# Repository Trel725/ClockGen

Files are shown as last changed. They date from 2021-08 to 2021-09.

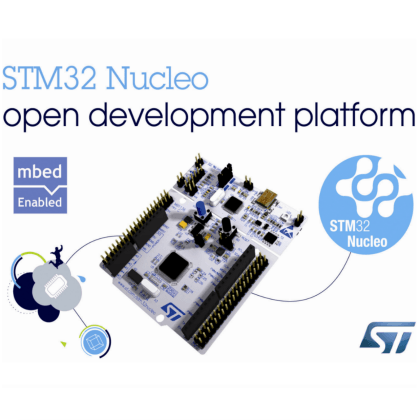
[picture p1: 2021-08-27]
hardware/PCBs/3V3_to_5/meta/board_stm32_nucleo_64.png

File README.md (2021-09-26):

# ClockGen

## What's that?

ClockGen is a project, devoted to developing a device that allow simple synchronization of scientific equipment. When experiments require synchronization, one might select do it with Arduino or similar hardware (LabJack?) which would give millisecond accuracy, or go far beyond that to specialized timing equipment, able of generating nanosecond precise pulses and costing thousands of euro. The goal of that project is to provide "something in between", a device which can provide microsecond accuracy at reasonable price. The devise is based on STM32F446RET Nucleo development board (price below 20 euro).

## Features?

 - Generating square wave at frequencies from 610 Hz (for 16 bit timer) or 0.009 Hz (for 32 bit timer) up to ~ 10 MHz
 - Programming arbitrary sequences of start, stop or change frequency events at 1 us accuracy 
 - Support of up to 10 timer channels for generating square wave
 - Synchronization of the generated signals with nanosecond accuracy by hardware synchronization
 - Up to 22 digital outputs, programmable to generate arbitrary sequences of on/off events with 1 us accuracy and nanosecond synchronization 
 - Hardware extension for Nucleo development board, converting LVTTL signals from microcontroller (3.3V) to standard TTL (5V)
 - Add-on hardware extension, converting 5V TTL signals to high-voltage signals (7-18V).

## How to use it

```python
from clockgen import ProgramGen
from clockgen.interface import TIM, GPIO
from clockgen.utils import send_program, start_execution

#instantiate HW
tim2 = TIM("TIM2")
tim5 = TIM("TIM5")
gpa = GPIO("GPIOA")

# turn on both timers at time 100us from program start
# tim2 at 20 kHz
tim2.on_sync(20_000, 100)
# and tim5 at 10 kHz
tim5.on_sync(10_000, 100)
# start them synchnously
tim2.start_sync(100)

# set 4th and 5th pins in GPIOA to high level at 120 us
gpa.on([4, 5], 120)
# then pin 4 to low level at 150 us
gpa.off(4, 150)
# and pin 5 at 900 us
gpa.off(5, 900)

# finally turn off the timers at 1000 us
tim2.off_sync(1000)
tim5.off_sync(1000)

# instantiate program generator
pg = ProgramGen()
# and generate the program, providing it list of used HW
prog = pg.generate_program([gpa, tim2, tim5])
# open the serial connection
ser = serial.Serial("/dev/ttyACM0", baudrate=1000000, timeout=5)
# and send the program to microntroller
send_program(prog)
# and start its execution:
start_execution()
```

Also, see folder examples.

## How does it work?

1. User describes the desired sequence of operations, like start signal generation at PA0 at 300 us.
2. Host-side program keeps track of all register changes and thus translates high-level operations into low-level
register manipulation
3. Host compiles sequence of register manipilation actions into binary program for micontroller and sends the program.
4. Microcontroller stores the program in RAM and waits for the start_execution command. As soon as command is received, it starts execution and generates required sequence of signals.

## What do I need to start using the ClockGen
In the simpliest case - just STM32F446RET Nucleo development board. As soon as your equipment recognizes LVTTL (3.3V) logical levels, it should suffice. Still, majority of scientific equipment works with 5V TTL levels, and behaviour might be unpredictable if different logical levels is used, thus it is recommeded to get extension board, which converts the signals to 5V TTL. Moreover, it is capable to supply more current and electrically isolates microcontroller from high voltage spikes.

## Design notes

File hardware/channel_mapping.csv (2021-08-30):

l | pin | tim | chan | port
0 | d2 | 1 | 3 | pa10
1 | d6 | 2 | 3 | pb10
2 | d4 | 3 | 2 | pb5
3 | d10 | 4 | 1 | pb6
4 | a0 | 5 | 1 | pa0
5 | d9 | 8 | 2 | pc7 | external clock
6 | d15 | 10 | 1 | pb8 | no slave
7 | d14 | 11 | 1 | pb9 | no slave
8 | d12 | 13 | 1 | pa6 | no slave
9 | d11 | 14 | 1 | pa7 | No slave

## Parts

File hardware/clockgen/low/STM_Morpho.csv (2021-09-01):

Reference | Value | Footprint | Datasheet
CN10 | Conn_02x19_Odd_Even | Connector_PinSocket_2.54mm:PinSocket_2x19_P2.54mm_Vertical | ~
U1 | 74ALVC164245DLG4 | footprints:74ALVC164245DLG4
R1 | 10K | Resistor_THT:R_Axial_DIN0207_L6.3mm_D2.5mm_P2.54mm_Vertical | ~
R2 | 10K | Resistor_THT:R_Axial_DIN0207_L6.3mm_D2.5mm_P2.54mm_Vertical | ~
U2 | 74ALVC164245DLG4 | footprints:74ALVC164245DLG4
C2 | CP | Capacitor_THT:CP_Radial_D5.0mm_P2.00mm | ~
C3.31 | C | Capacitor_SMD:C_0805_2012Metric | ~
C5V1 | C | Capacitor_SMD:C_0805_2012Metric | ~
C5V2 | C | Capacitor_SMD:C_0805_2012Metric | ~
C3.32 | C | Capacitor_SMD:C_0805_2012Metric | ~
C1 | CP | Capacitor_THT:CP_Radial_D5.0mm_P2.00mm | ~
J1 | Conn_02x20_Odd_Even | Connector_PinHeader_2.54mm:PinHeader_2x20_P2.54mm_Vertical | ~
CN7 | Conn_02x19_Odd_Even | Connector_PinSocket_2.54mm:PinSocket_2x19_P2.54mm_Vertical | ~

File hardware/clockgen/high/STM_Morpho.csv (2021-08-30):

Reference | Value | Footprint | Datasheet
U1 | CD40109BNSR | CD40109BNSR:CD40109BNSR
U2 | CD40109BNSR | CD40109BNSR:CD40109BNSR
U3 | CD40109BNSR | CD40109BNSR:CD40109BNSR
U4 | CD40109BNSR | CD40109BNSR:CD40109BNSR
U5 | CD40109BNSR | CD40109BNSR:CD40109BNSR
U6 | CD40109BNSR | CD40109BNSR:CD40109BNSR
U7 | CD40109BNSR | CD40109BNSR:CD40109BNSR
U8 | CD40109BNSR | CD40109BNSR:CD40109BNSR
C4 | CP | Capacitor_THT:CP_Radial_D5.0mm_P2.00mm | ~
CHIGH3 | C | Capacitor_SMD:C_1206_3216Metric | ~
CHIGH6 | C | Capacitor_SMD:C_1206_3216Metric | ~
CHIGH1 | C | Capacitor_SMD:C_1206_3216Metric | ~
CHIGH4 | C | Capacitor_SMD:C_1206_3216Metric | ~
CHIGH7 | C | Capacitor_SMD:C_1206_3216Metric | ~
CHIGH8 | C | Capacitor_SMD:C_1206_3216Metric | ~
CHIGH2 | C | Capacitor_SMD:C_1206_3216Metric | ~
CHIGH5 | C | Capacitor_SMD:C_1206_3216Metric | ~
J2 | Conn_02x20_Odd_Even | Connector_PinHeader_2.54mm:PinHeader_2x20_P2.54mm_Vertical | ~
J1 | Conn_02x20_Odd_Even | Connector_PinHeader_2.54mm:PinHeader_2x20_P2.54mm_Vertical | ~
R1 | 1K | Resistor_THT:R_Axial_DIN0207_L6.3mm_D2.5mm_P2.54mm_Vertical | ~
J3 | Conn_01x02_Female | TerminalBlock_Phoenix:TerminalBlock_Phoenix_PT-1,5-2-3.5-H_1x02_P3.50mm_Horizontal | ~
C1 | CP | Capacitor_THT:CP_Radial_D5.0mm_P2.00mm | ~

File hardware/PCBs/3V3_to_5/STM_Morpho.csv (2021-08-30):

Reference | Value | Footprint | Datasheet
CN10 | Conn_02x19_Odd_Even | Connector_PinSocket_2.54mm:PinSocket_2x19_P2.54mm_Vertical | ~
U1 | 74ALVC164245DLG4 | footprints:74ALVC164245DLG4
R1 | 10K | Resistor_THT:R_Axial_DIN0207_L6.3mm_D2.5mm_P2.54mm_Vertical | ~
R2 | 10K | Resistor_THT:R_Axial_DIN0207_L6.3mm_D2.5mm_P2.54mm_Vertical | ~
U2 | 74ALVC164245DLG4 | footprints:74ALVC164245DLG4
C2 | CP | Capacitor_THT:CP_Radial_D5.0mm_P2.00mm | ~
C3.31 | C | Capacitor_SMD:C_0805_2012Metric | ~
C5V1 | C | Capacitor_SMD:C_0805_2012Metric | ~
C5V2 | C | Capacitor_SMD:C_0805_2012Metric | ~
C3.32 | C | Capacitor_SMD:C_0805_2012Metric | ~
C1 | CP | Capacitor_THT:CP_Radial_D5.0mm_P2.00mm | ~
J1 | Conn_02x20_Odd_Even | Connector_PinHeader_2.54mm:PinHeader_2x20_P2.54mm_Vertical | ~
CN7 | Conn_02x19_Odd_Even | Connector_PinSocket_2.54mm:PinSocket_2x19_P2.54mm_Vertical | ~
J1 | Conn_02x20_Odd_Even | Connector_PinHeader_2.54mm:PinHeader_2x20_P2.54mm_Vertical | ~
J3 | Screw_Terminal_01x08 | TerminalBlock_Phoenix:TerminalBlock_Phoenix_PT-1,5-8-3.5-H_1x08_P3.50mm_Horizontal | ~
J2 | Screw_Terminal_01x08 | TerminalBlock_Phoenix:TerminalBlock_Phoenix_PT-1,5-8-3.5-H_1x08_P3.50mm_Horizontal | ~
J5 | Screw_Terminal_01x08 | TerminalBlock_Phoenix:TerminalBlock_Phoenix_PT-1,5-8-3.5-H_1x08_P3.50mm_Horizontal | ~
J4 | Screw_Terminal_01x08 | TerminalBlock_Phoenix:TerminalBlock_Phoenix_PT-1,5-8-3.5-H_1x08_P3.50mm_Horizontal | ~
J6 | Screw_Terminal_01x08 | TerminalBlock_Phoenix:TerminalBlock_Phoenix_PT-1,5-8-3.5-H_1x08_P3.50mm_Horizontal | ~
J7 | Screw_Terminal_01x08 | TerminalBlock_Phoenix:TerminalBlock_Phoenix_PT-1,5-8-3.5-H_1x08_P3.50mm_Horizontal | ~
J8 | Screw_Terminal_01x08 | TerminalBlock_Phoenix:TerminalBlock_Phoenix_PT-1,5-8-3.5-H_1x08_P3.50mm_Horizontal | ~
J9 | Screw_Terminal_01x08 | TerminalBlock_Phoenix:TerminalBlock_Phoenix_PT-1,5-8-3.5-H_1x08_P3.50mm_Horizontal | ~
U1 | CD40109BNSR | CD40109BNSR:CD40109BNSR
U2 | CD40109BNSR | CD40109BNSR:CD40109BNSR
U3 | CD40109BNSR | CD40109BNSR:CD40109BNSR
U4 | CD40109BNSR | CD40109BNSR:CD40109BNSR
U5 | CD40109BNSR | CD40109BNSR:CD40109BNSR
U6 | CD40109BNSR | CD40109BNSR:CD40109BNSR
U7 | CD40109BNSR | CD40109BNSR:CD40109BNSR
U8 | CD40109BNSR | CD40109BNSR:CD40109BNSR
C4 | CP | Capacitor_THT:CP_Radial_D5.0mm_P2.00mm | ~
CHIGH3 | C | Capacitor_SMD:C_1206_3216Metric | ~
CHIGH6 | C | Capacitor_SMD:C_1206_3216Metric | ~
CHIGH1 | C | Capacitor_SMD:C_1206_3216Metric | ~
CHIGH4 | C | Capacitor_SMD:C_1206_3216Metric | ~
CHIGH7 | C | Capacitor_SMD:C_1206_3216Metric | ~
CHIGH8 | C | Capacitor_SMD:C_1206_3216Metric | ~
CHIGH2 | C | Capacitor_SMD:C_1206_3216Metric | ~
CHIGH5 | C | Capacitor_SMD:C_1206_3216Metric | ~
J2 | Conn_02x20_Odd_Even | Connector_PinHeader_2.54mm:PinHeader_2x20_P2.54mm_Vertical | ~
J1 | Conn_02x20_Odd_Even | Connector_PinHeader_2.54mm:PinHeader_2x20_P2.54mm_Vertical | ~
R1 | 1K | Resistor_THT:R_Axial_DIN0207_L6.3mm_D2.5mm_P2.54mm_Vertical | ~
J3 | Conn_01x02_Female | TerminalBlock_Phoenix:TerminalBlock_Phoenix_PT-1,5-2-3.5-H_1x02_P3.50mm_Horizontal | ~
C1 | CP | Capacitor_THT:CP_Radial_D5.0mm_P2.00mm | ~

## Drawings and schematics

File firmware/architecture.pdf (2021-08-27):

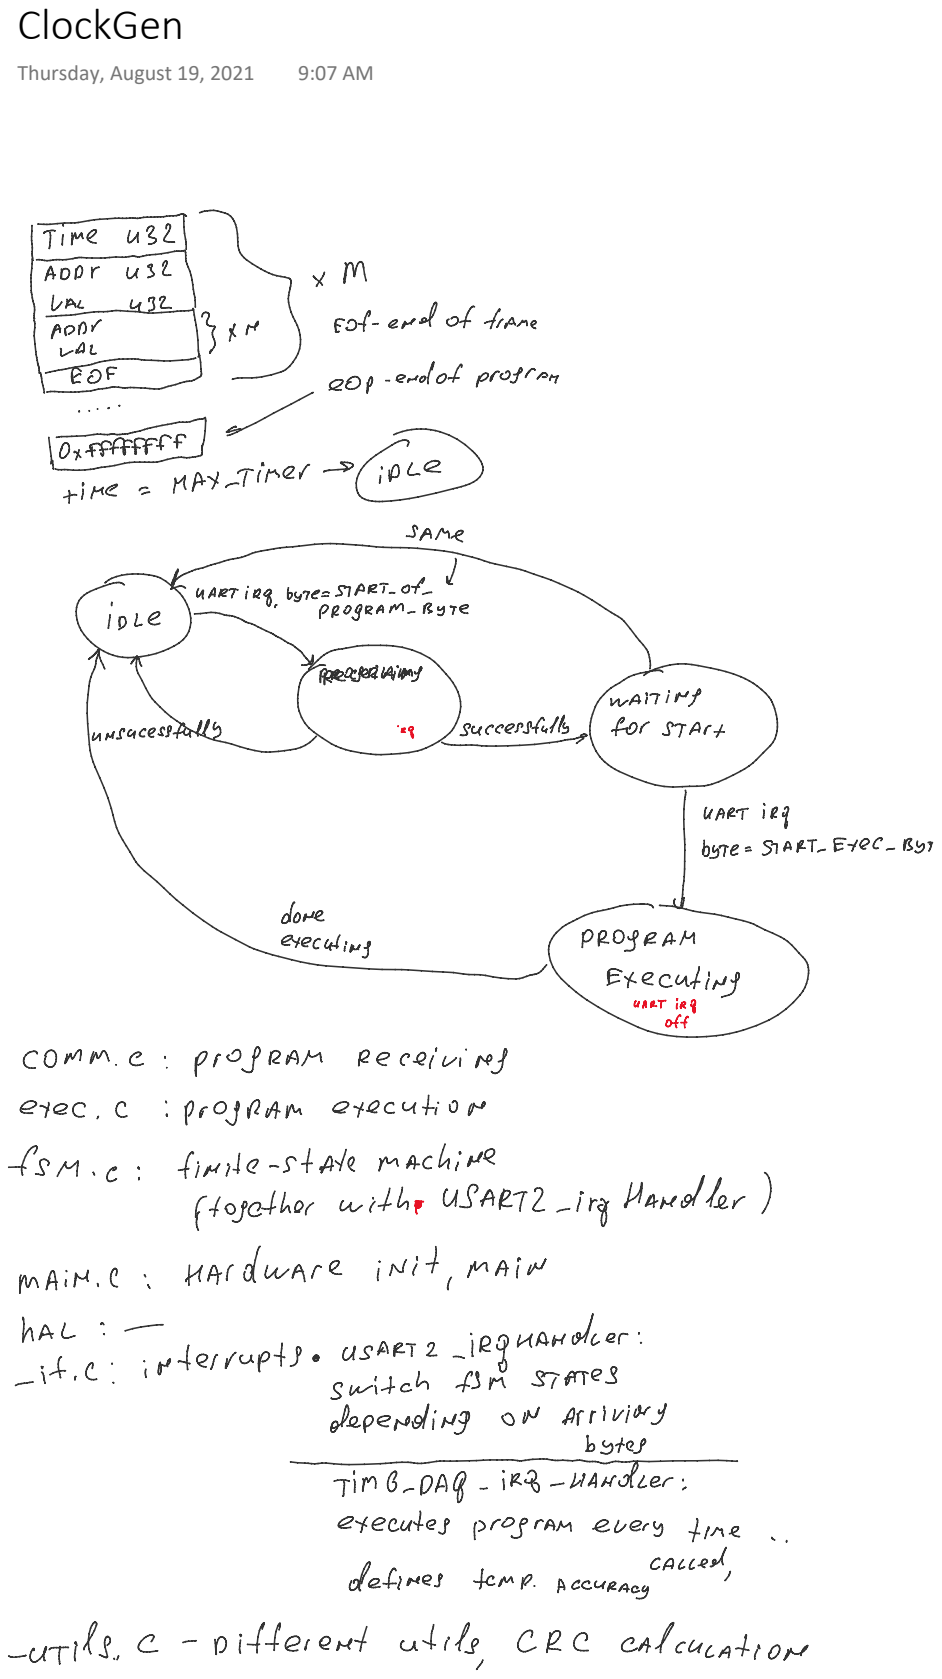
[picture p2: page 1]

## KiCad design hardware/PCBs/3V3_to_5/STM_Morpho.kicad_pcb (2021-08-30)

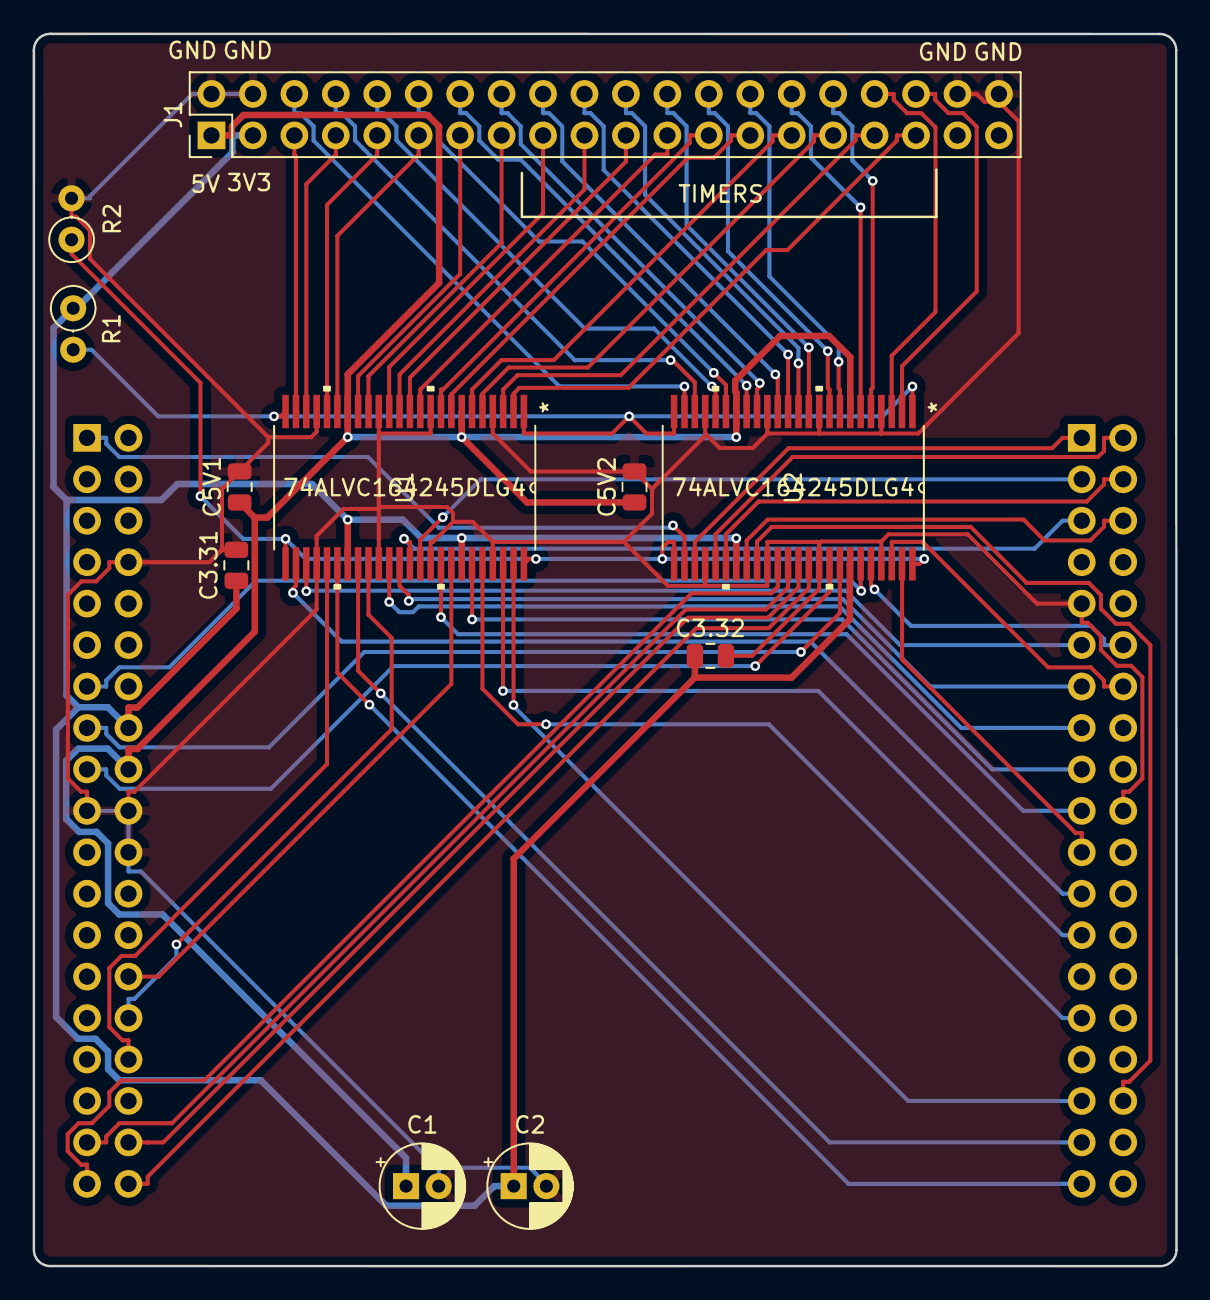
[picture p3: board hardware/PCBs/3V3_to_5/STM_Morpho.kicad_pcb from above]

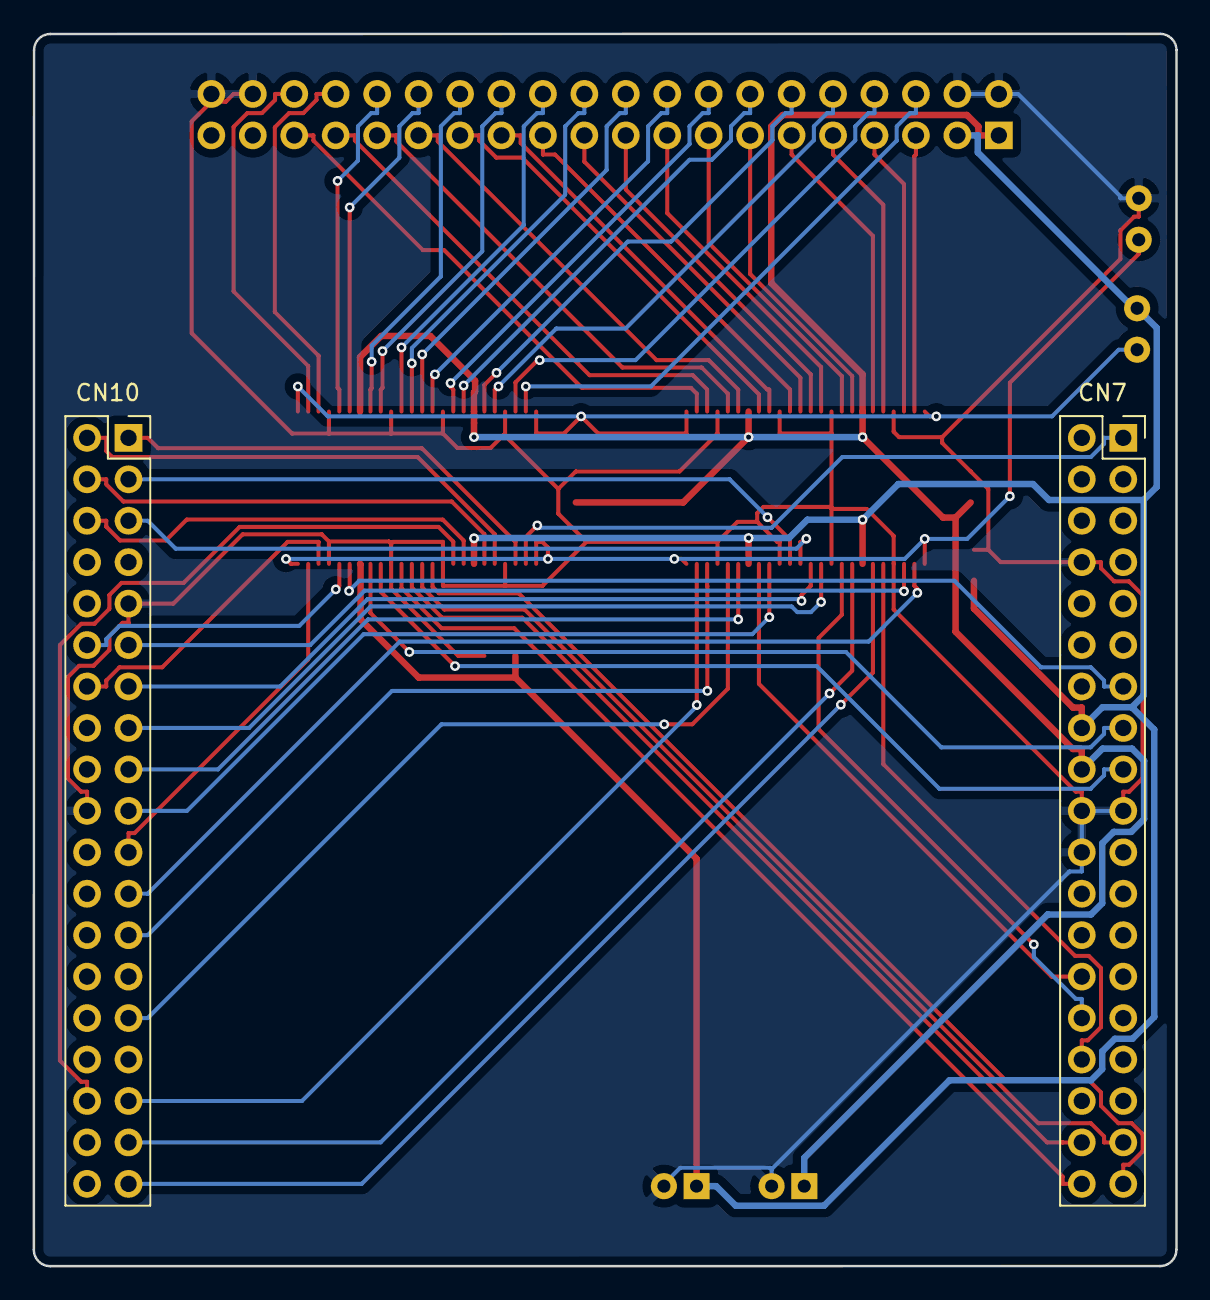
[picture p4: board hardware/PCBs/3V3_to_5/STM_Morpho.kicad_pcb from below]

Board: 2 copper layers, 70.0 x 75.5 mm, 13 parts (2 on the bottom side), 69 nets.

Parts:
C1, C2: CP; CP_Radial_D5.0mm_P2.00mm
C3.31, C3.32, C5V1, C5V2: C; C_0805_2012Metric
CN7, CN10: Conn_02x19_Odd_Even; PinSocket_2x19_P2.54mm_Vertical
J1: Conn_02x20_Odd_Even; PinHeader_2x20_P2.54mm_Vertical
R1, R2: 10K; R_Axial_DIN0207_L6.3mm_D2.5mm_P2.54mm_Vertical
U1, U2: 74ALVC164245DLG4

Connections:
+3V3: C2.1, C3.31.1, C3.32.1, CN7.16, J1.3, R1.1, U1.31, U1.42, U2.31, U2.42
+5V: C1.1, C5V1.1, C5V2.1, CN7.18, J1.1, U1.7, U1.18, U2.7, U2.18
/PA0: CN7.28, U1.41
/PA0_5V: J1.27, U1.8
/PA1: CN7.30, U1.33
/PA1_5V: J1.15, U1.16
/PA2: CN10.35, U1.32
/PA2_5V: J1.13, U1.17
/PA3: CN10.37, U1.30
/PA3_5V: J1.11, U1.19
/PA4: CN7.32, U1.29
/PA4_5V: J1.9, U1.20
/PA5: CN10.11, U1.27
/PA5_5V: J1.7, U1.22
/PA6: CN10.13, U1.36
/PA6_5V: J1.19, U1.13
/PA7: CN10.15, U1.35
/PA7_5V: J1.17, U1.14
/PA8: CN10.23, U1.26
/PA8_5V: J1.5, U1.23
/PA9: CN10.21, U2.47
/PA9_5V: J1.36, U2.2
/PA10: CN10.33, U1.47
/PA10_5V: J1.35, U1.2
/PA11: CN10.14, U2.46
/PA11_5V: J1.34, U2.3
/PA12: CN10.12, U2.44
/PA12_5V: J1.32, U2.5
/PA13: CN7.13, U2.43
/PA13_5V: J1.30, U2.6
/PA14: CN7.15, U2.41
/PA14_5V: J1.28, U2.8
/PA15: CN7.17, U2.40
/PA15_5V: J1.26, U2.9
/PB5: CN10.29, U1.44
/PB5_5V: J1.31, U1.5
/PB6: CN10.17, U1.43
/PB6_5V: J1.29, U1.6
/PB8: CN10.3, U1.38
/PB8_5V: J1.23, U1.11
/PB9: CN10.5, U1.37
/PB9_5V: J1.21, U1.12
/PB10: CN10.25, U1.46
/PB10_5V: J1.33, U1.3
/PC0: CN7.38, U2.38
/PC0_5V: J1.24, U2.11
/PC1: CN7.36, U2.37
/PC1_5V: J1.22, U2.12
/PC2: CN7.35, U2.36
/PC2_5V: J1.20, U2.13
/PC3: CN7.37, U2.35
/PC3_5V: J1.18, U2.14
/PC4: CN10.34, U2.33
/PC4_5V: J1.16, U2.16
/PC5: CN10.6, U2.32
/PC5_5V: J1.14, U2.17
/PC6: CN10.4, U2.30
/PC6_5V: J1.12, U2.19
/PC7: CN10.19, U1.40
/PC7_5V: J1.25, U1.9
/PC8: CN10.2, U2.29
/PC8_5V: J1.10, U2.20
/PC9: CN10.1, U2.27
/PC9_5V: J1.8, U2.22
/PC10: CN7.1, U2.26
/PC10_5V: J1.6, U2.23
/PULLDOWN: R2.1, U1.25, U1.48, U2.25, U2.48
/PULLUP: R1.2, U1.1, U1.24, U2.1, U2.24
GND: C1.2, C2.2, C3.31.2, C3.32.2, C5V1.2, C5V2.2, CN7.8, CN7.19, CN7.20, CN7.22, CN10.9, CN10.20, J1.2, J1.4, J1.38, J1.40, R2.2, U1.4, U1.10, U1.15, U1.21, U1.28, U1.34, U1.39, U1.45, U2.4, U2.10, U2.15, U2.21, U2.28, U2.34, U2.39, U2.45

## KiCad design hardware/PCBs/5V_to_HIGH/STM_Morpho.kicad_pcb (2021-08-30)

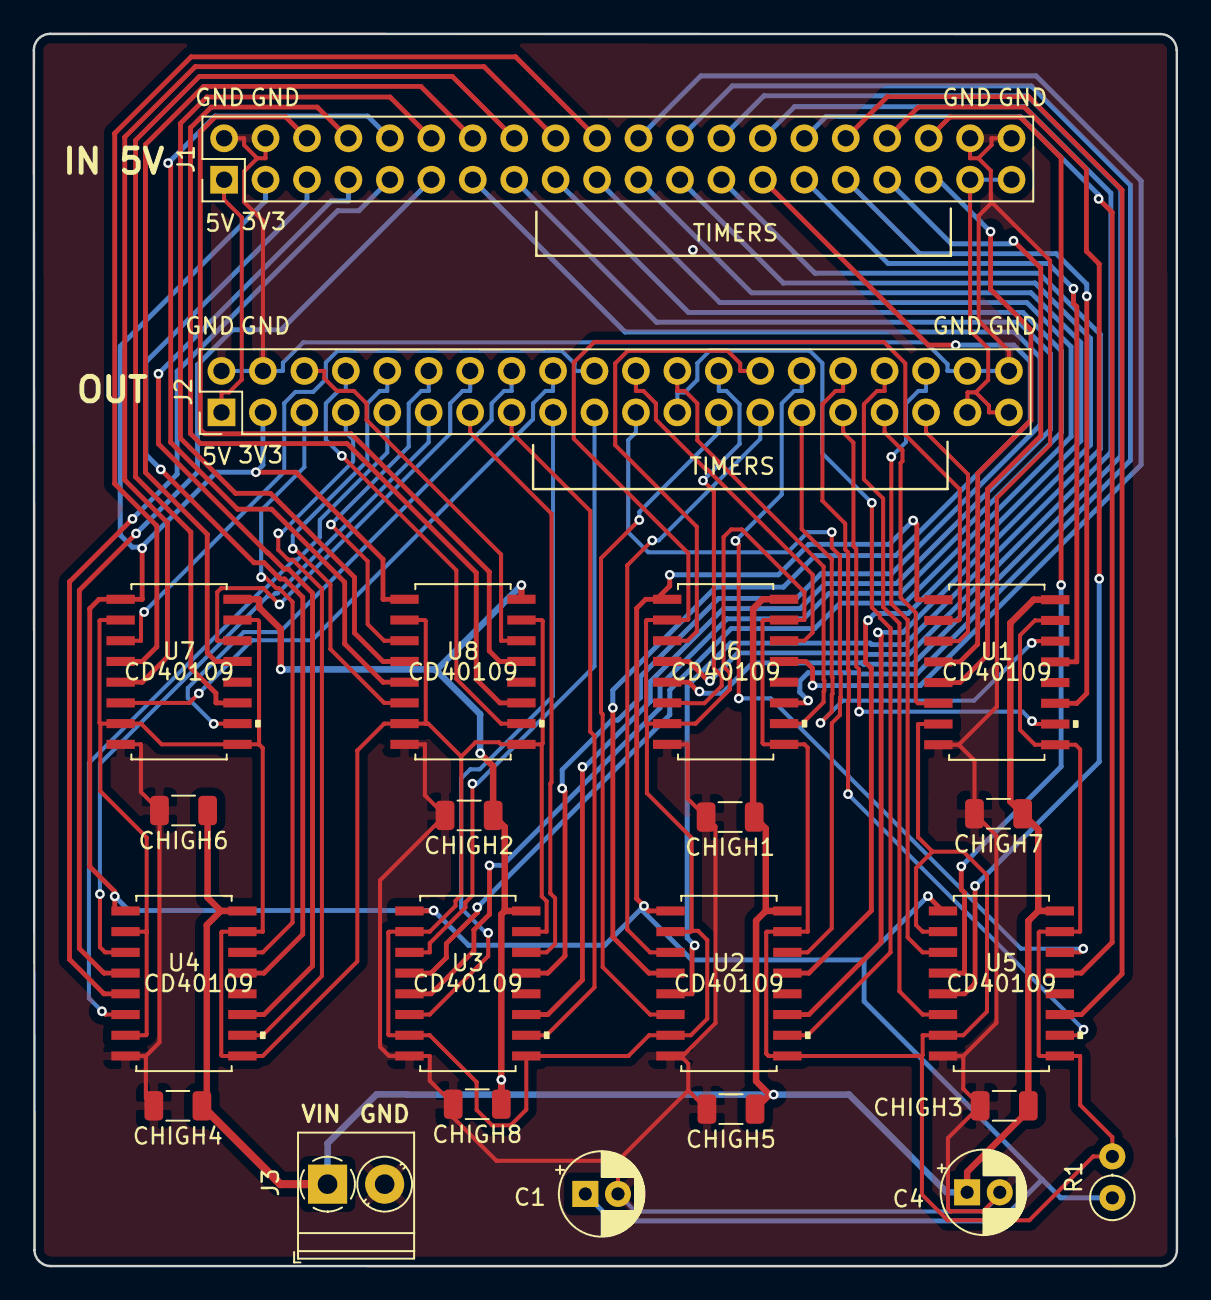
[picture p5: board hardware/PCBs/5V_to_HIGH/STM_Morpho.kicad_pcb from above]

Board: 2 copper layers, 70.1 x 75.5 mm, 22 parts (0 on the bottom side), 70 nets.

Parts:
C1, C4: CP; CP_Radial_D5.0mm_P2.00mm
CHIGH1, CHIGH2, CHIGH3, CHIGH4, CHIGH5, CHIGH6, CHIGH7, CHIGH8: C; C_1206_3216Metric
J1, J2: Conn_02x20_Odd_Even; PinHeader_2x20_P2.54mm_Vertical
J3: Conn_01x02_Female; TerminalBlock_Phoenix_PT-1,5-2-3.5-H_1x02_P3.50mm_Horizontal
R1: 1K; R_Axial_DIN0207_L6.3mm_D2.5mm_P2.54mm_Vertical
U1, U2, U3, U4, U5, U6, U7, U8: CD40109; CD40109BNSR

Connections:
+3V3: C1.1, J1.3, J2.3, R1.1, U1.1, U2.1, U3.1, U4.1, U5.1, U6.1, U7.1, U8.1
+15V: C4.1, CHIGH1.1, CHIGH2.1, CHIGH3.1, CHIGH4.1, CHIGH5.1, CHIGH6.1, CHIGH7.1, CHIGH8.1, J3.1, U1.16, U2.16, U3.16, U4.16, U5.16, U6.16, U7.16, U8.16
/+5V: J1.1, J2.1
/NC: J1.37, J1.39, J2.37, J2.39
/PA0_5V: J2.27, U2.3
/PA0_HIGH: J1.27, U2.4
/PA1_5V: J2.15, U3.10
/PA1_HIGH: J1.15, U3.11
/PA2_5V: J2.13, U3.14
/PA2_HIGH: J1.13, U3.13
/PA3_5V: J2.11, U4.3
/PA3_HIGH: J1.11, U4.4
/PA4_5V: J2.9, U4.6
/PA4_HIGH: J1.9, U4.5
/PA5_5V: J2.7, U4.10
/PA5_HIGH: J1.7, U4.11
/PA6_5V: J2.19, U3.3
/PA6_HIGH: J1.19, U3.4
/PA7_5V: J2.17, U3.6
/PA7_HIGH: J1.17, U3.5
/PA8_5V: J2.5, U4.14
/PA8_HIGH: J1.5, U4.13
/PA9_5V: J2.36, U5.3
/PA9_HIGH: J1.36, U5.4
/PA10_5V: J2.35, U1.3
/PA10_HIGH: J1.35, U1.4
/PA11_5V: J2.34, U5.6
/PA11_HIGH: J1.34, U5.5
/PA12_5V: J2.32, U5.10
/PA12_HIGH: J1.32, U5.11
/PA13_5V: J2.30, U5.14
/PA13_HIGH: J1.30, U5.13
/PA14_5V: J2.28, U6.3
/PA14_HIGH: J1.28, U6.4
/PA15_5V: J2.26, U6.6
/PA15_HIGH: J1.26, U6.5
/PB5_5V: J2.31, U1.10
/PB5_HIGH: J1.31, U1.11
/PB6_5V: J2.29, U1.14
/PB6_HIGH: J1.29, U1.13
/PB8_5V: J2.23, U2.10
/PB8_HIGH: J1.23, U2.11
/PB9_5V: J2.21, U2.14
/PB9_HIGH: J1.21, U2.13
/PB10_5V: J2.33, U1.6
/PB10_HIGH: J1.33, U1.5
/PC0_5V: J2.24, U6.10
/PC0_HIGH: J1.24, U6.11
/PC1_5V: J2.22, U6.14
/PC1_HIGH: J1.22, U6.13
/PC2_5V: J2.20, U7.3
/PC2_HIGH: J1.20, U7.4
/PC3_5V: J2.18, U7.6
/PC3_HIGH: J1.18, U7.5
/PC4_5V: J2.16, U7.10
/PC4_HIGH: J1.16, U7.11
/PC5_5V: J2.14, U7.14
/PC5_HIGH: J1.14, U7.13
/PC6_5V: J2.12, U8.3
/PC6_HIGH: J1.12, U8.4
/PC7_5V: J2.25, U2.6
/PC7_HIGH: J1.25, U2.5
/PC8_5V: J2.10, U8.6
/PC8_HIGH: J1.10, U8.5
/PC9_5V: J2.8, U8.10
/PC9_HIGH: J1.8, U8.11
/PC10_5V: J2.6, U8.14
/PC10_HIGH: J1.6, U8.13
/PULLUP_HIGH: R1.2, U1.2, U1.7, U1.9, U1.15, U2.2, U2.7, U2.9, U2.15, U3.2, U3.7, U3.9, U3.15, U4.2, U4.7, U4.9, U4.15, U5.2, U5.7, U5.9, U5.15, U6.2, U6.7, U6.9, U6.15, U7.2, U7.7, U7.9, U7.15, U8.2, U8.7, U8.9, U8.15
GND: C1.2, C4.2, CHIGH1.2, CHIGH2.2, CHIGH3.2, CHIGH4.2, CHIGH5.2, CHIGH6.2, CHIGH7.2, CHIGH8.2, J1.2, J1.4, J1.38, J1.40, J2.2, J2.4, J2.38, J2.40, J3.2, U1.8, U2.8, U3.8, U4.8, U5.8, U6.8, U7.8, U8.8

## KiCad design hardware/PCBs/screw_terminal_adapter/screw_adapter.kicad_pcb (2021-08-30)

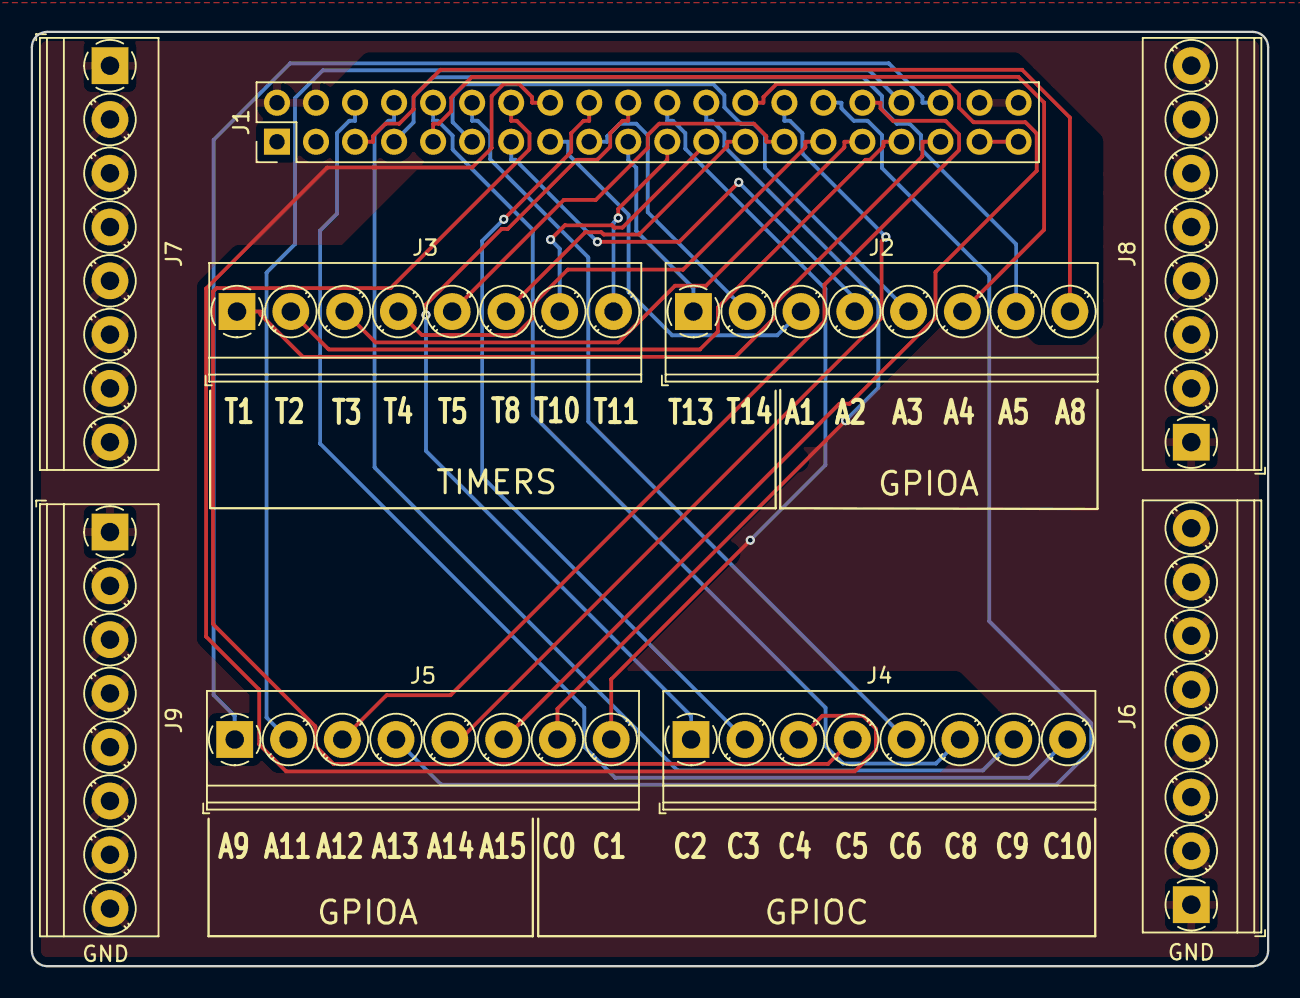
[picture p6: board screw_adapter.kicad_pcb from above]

Board: 2 copper layers, 80.5 x 60.8 mm, 9 parts (0 on the bottom side), 34 nets.

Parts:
J1: Conn_02x20_Odd_Even; PinHeader_2x20_P2.54mm_Vertical
J2, J3, J4, J5, J6, J7, J8, J9: Screw_Terminal_01x08; TerminalBlock_Phoenix_PT-1,5-8-3.5-H_1x08_P3.50mm_Horizontal

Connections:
/NC: J1.37, J1.39
/PA0_5V: J1.27, J3.5
/PA1_5V: J1.15, J2.3
/PA2_5V: J1.13, J2.4
/PA3_5V: J1.11, J2.5
/PA4_5V: J1.9, J2.6
/PA5_5V: J1.7, J2.7
/PA6_5V: J1.19, J2.1
/PA7_5V: J1.17, J2.2
/PA8_5V: J1.5, J2.8
/PA9_5V: J1.36, J5.1
/PA10_5V: J1.35, J3.1
/PA11_5V: J1.34, J5.2
/PA12_5V: J1.32, J5.3
/PA13_5V: J1.30, J5.4
/PA14_5V: J1.28, J5.5
/PA15_5V: J1.26, J5.6
/PB5_5V: J1.31, J3.3
/PB6_5V: J1.29, J3.4
/PB8_5V: J1.23, J3.7
/PB9_5V: J1.21, J3.8
/PB10_5V: J1.33, J3.2
/PC0_5V: J1.24, J5.7
/PC1_5V: J1.22, J5.8
/PC2_5V: J1.20, J4.1
/PC3_5V: J1.18, J4.2
/PC4_5V: J1.16, J4.3
/PC5_5V: J1.14, J4.4
/PC6_5V: J1.12, J4.5
/PC7_5V: J1.25, J3.6
/PC8_5V: J1.10, J4.6
/PC9_5V: J1.8, J4.7
/PC10_5V: J1.6, J4.8
GND: J1.2, J1.4, J1.38, J1.40, J6.1, J6.2, J6.3, J6.4, J6.5, J6.6, J6.7, J6.8, J7.1, J7.2, J7.3, J7.4, J7.5, J7.6, J7.7, J7.8, J8.1, J8.2, J8.3, J8.4, J8.5, J8.6, J8.7, J8.8, J9.1, J9.2, J9.3, J9.4, J9.5, J9.6, J9.7, J9.8

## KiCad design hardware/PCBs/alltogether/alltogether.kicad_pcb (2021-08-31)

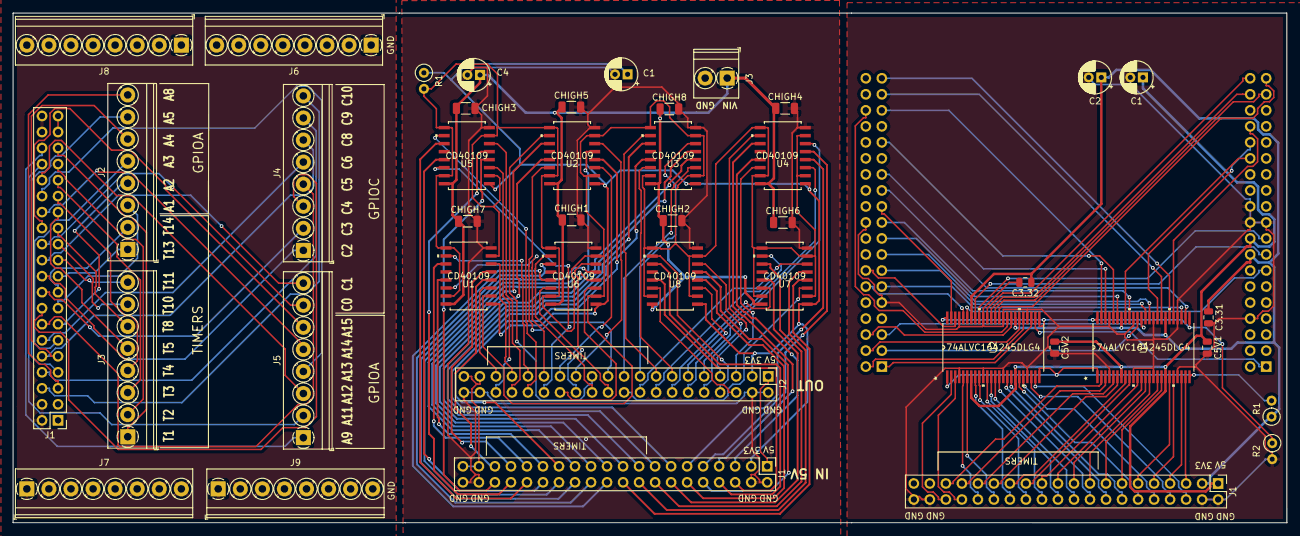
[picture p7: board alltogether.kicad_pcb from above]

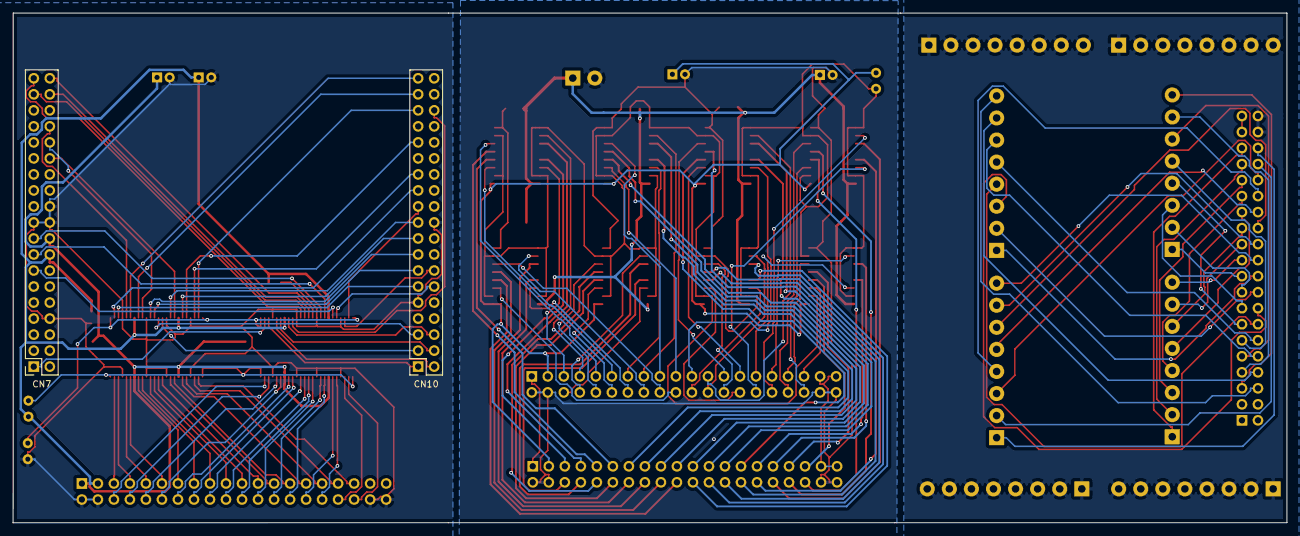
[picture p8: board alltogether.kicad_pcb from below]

Board: 2 copper layers, 202.0 x 80.8 mm, 44 parts (2 on the bottom side), 105 nets.

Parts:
C1, C1#2, C2, C4: CP; CP_Radial_D5.0mm_P2.00mm
C3.31, C3.32, C5V1, C5V2: C; C_0805_2012Metric
CHIGH1, CHIGH2, CHIGH3, CHIGH4, CHIGH5, CHIGH6, CHIGH7, CHIGH8: C; C_1206_3216Metric
CN7, CN10: Conn_02x19_Odd_Even; PinSocket_2x19_P2.54mm_Vertical
J1, J1#2, J1#3, J2#2: Conn_02x20_Odd_Even; PinHeader_2x20_P2.54mm_Vertical
J2, J3, J4, J5, J6, J7, J8, J9: Screw_Terminal_01x08; TerminalBlock_Phoenix_PT-1,5-8-3.5-H_1x08_P3.50mm_Horizontal
J3#2: Conn_01x02_Female; TerminalBlock_Phoenix_PT-1,5-2-3.5-H_1x02_P3.50mm_Horizontal
R1: 1K; R_Axial_DIN0207_L6.3mm_D2.5mm_P2.54mm_Vertical
R1#2, R2: 10K; R_Axial_DIN0207_L6.3mm_D2.5mm_P2.54mm_Vertical
U1, U2, U3, U4, U5, U6, U7, U8: CD40109; CD40109BNSR
U1#2, U2#2: 74ALVC164245DLG4

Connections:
+3V3: C1.1, C2.1, C3.31.1, C3.32.1, CN7.16, J1#2.3, J1#3.3, J2#2.3, R1.1, R1#2.1, U1.1, U1#2.31, U1#2.42, U2.1, U2#2.31, U2#2.42, U3.1, U4.1, U5.1, U6.1, U7.1, U8.1
+5V: C1#2.1, C5V1.1, C5V2.1, CN7.18, J1#3.1, U1#2.7, U1#2.18, U2#2.7, U2#2.18
+15V: C4.1, CHIGH1.1, CHIGH2.1, CHIGH3.1, CHIGH4.1, CHIGH5.1, CHIGH6.1, CHIGH7.1, CHIGH8.1, J3#2.1, U1.16, U2.16, U3.16, U4.16, U5.16, U6.16, U7.16, U8.16
/+5V: J1#2.1, J2#2.1
/NC: J1.37, J1.39, J1#2.37, J1#2.39, J2#2.37, J2#2.39
/PA0: CN7.28, U1#2.41
/PA0_5V: J1.27, J1#3.27, J2#2.27, J3.5, U1#2.8, U2.3
/PA0_HIGH: J1#2.27, U2.4
/PA1: CN7.30, U1#2.33
/PA1_5V: J1.15, J1#3.15, J2.3, J2#2.15, U1#2.16, U3.10
/PA1_HIGH: J1#2.15, U3.11
/PA2: CN10.35, U1#2.32
/PA2_5V: J1.13, J1#3.13, J2.4, J2#2.13, U1#2.17, U3.14
/PA2_HIGH: J1#2.13, U3.13
/PA3: CN10.37, U1#2.30
/PA3_5V: J1.11, J1#3.11, J2.5, J2#2.11, U1#2.19, U4.3
/PA3_HIGH: J1#2.11, U4.4
/PA4: CN7.32, U1#2.29
/PA4_5V: J1.9, J1#3.9, J2.6, J2#2.9, U1#2.20, U4.6
/PA4_HIGH: J1#2.9, U4.5
/PA5: CN10.11, U1#2.27
/PA5_5V: J1.7, J1#3.7, J2.7, J2#2.7, U1#2.22, U4.10
/PA5_HIGH: J1#2.7, U4.11
/PA6: CN10.13, U1#2.36
/PA6_5V: J1.19, J1#3.19, J2.1, J2#2.19, U1#2.13, U3.3
/PA6_HIGH: J1#2.19, U3.4
/PA7: CN10.15, U1#2.35
/PA7_5V: J1.17, J1#3.17, J2.2, J2#2.17, U1#2.14, U3.6
/PA7_HIGH: J1#2.17, U3.5
/PA8: CN10.23, U1#2.26
/PA8_5V: J1.5, J1#3.5, J2.8, J2#2.5, U1#2.23, U4.14
/PA8_HIGH: J1#2.5, U4.13
/PA9: CN10.21, U2#2.47
/PA9_5V: J1.36, J1#3.36, J2#2.36, J5.1, U2#2.2, U5.3
/PA9_HIGH: J1#2.36, U5.4
/PA10: CN10.33, U1#2.47
/PA10_5V: J1.35, J1#3.35, J2#2.35, J3.1, U1.3, U1#2.2
/PA10_HIGH: J1#2.35, U1.4
/PA11: CN10.14, U2#2.46
/PA11_5V: J1.34, J1#3.34, J2#2.34, J5.2, U2#2.3, U5.6
/PA11_HIGH: J1#2.34, U5.5
/PA12: CN10.12, U2#2.44
/PA12_5V: J1.32, J1#3.32, J2#2.32, J5.3, U2#2.5, U5.10
/PA12_HIGH: J1#2.32, U5.11
/PA13: CN7.13, U2#2.43
/PA13_5V: J1.30, J1#3.30, J2#2.30, J5.4, U2#2.6, U5.14
/PA13_HIGH: J1#2.30, U5.13
/PA14: CN7.15, U2#2.41
/PA14_5V: J1.28, J1#3.28, J2#2.28, J5.5, U2#2.8, U6.3
/PA14_HIGH: J1#2.28, U6.4
/PA15: CN7.17, U2#2.40
/PA15_5V: J1.26, J1#3.26, J2#2.26, J5.6, U2#2.9, U6.6
/PA15_HIGH: J1#2.26, U6.5
/PB5: CN10.29, U1#2.44
/PB5_5V: J1.31, J1#3.31, J2#2.31, J3.3, U1.10, U1#2.5
/PB5_HIGH: J1#2.31, U1.11
/PB6: CN10.17, U1#2.43
/PB6_5V: J1.29, J1#3.29, J2#2.29, J3.4, U1.14, U1#2.6
/PB6_HIGH: J1#2.29, U1.13
/PB8: CN10.3, U1#2.38
/PB8_5V: J1.23, J1#3.23, J2#2.23, J3.7, U1#2.11, U2.10
/PB8_HIGH: J1#2.23, U2.11
/PB9: CN10.5, U1#2.37
/PB9_5V: J1.21, J1#3.21, J2#2.21, J3.8, U1#2.12, U2.14
/PB9_HIGH: J1#2.21, U2.13
/PB10: CN10.25, U1#2.46
/PB10_5V: J1.33, J1#3.33, J2#2.33, J3.2, U1.6, U1#2.3
/PB10_HIGH: J1#2.33, U1.5
/PC0: CN7.38, U2#2.38
/PC0_5V: J1.24, J1#3.24, J2#2.24, J5.7, U2#2.11, U6.10
/PC0_HIGH: J1#2.24, U6.11
/PC1: CN7.36, U2#2.37
/PC1_5V: J1.22, J1#3.22, J2#2.22, J5.8, U2#2.12, U6.14
/PC1_HIGH: J1#2.22, U6.13
/PC2: CN7.35, U2#2.36
/PC2_5V: J1.20, J1#3.20, J2#2.20, J4.1, U2#2.13, U7.3
/PC2_HIGH: J1#2.20, U7.4
/PC3: CN7.37, U2#2.35
/PC3_5V: J1.18, J1#3.18, J2#2.18, J4.2, U2#2.14, U7.6
/PC3_HIGH: J1#2.18, U7.5
/PC4: CN10.34, U2#2.33
/PC4_5V: J1.16, J1#3.16, J2#2.16, J4.3, U2#2.16, U7.10
/PC4_HIGH: J1#2.16, U7.11
/PC5: CN10.6, U2#2.32
/PC5_5V: J1.14, J1#3.14, J2#2.14, J4.4, U2#2.17, U7.14
/PC5_HIGH: J1#2.14, U7.13
/PC6: CN10.4, U2#2.30
/PC6_5V: J1.12, J1#3.12, J2#2.12, J4.5, U2#2.19, U8.3
/PC6_HIGH: J1#2.12, U8.4
/PC7: CN10.19, U1#2.40
/PC7_5V: J1.25, J1#3.25, J2#2.25, J3.6, U1#2.9, U2.6
/PC7_HIGH: J1#2.25, U2.5
/PC8: CN10.2, U2#2.29
/PC8_5V: J1.10, J1#3.10, J2#2.10, J4.6, U2#2.20, U8.6
/PC8_HIGH: J1#2.10, U8.5
/PC9: CN10.1, U2#2.27
/PC9_5V: J1.8, J1#3.8, J2#2.8, J4.7, U2#2.22, U8.10
/PC9_HIGH: J1#2.8, U8.11
/PC10: CN7.1, U2#2.26
/PC10_5V: J1.6, J1#3.6, J2#2.6, J4.8, U2#2.23, U8.14
/PC10_HIGH: J1#2.6, U8.13
/PULLDOWN: R2.1, U1#2.25, U1#2.48, U2#2.25, U2#2.48
/PULLUP: R1#2.2, U1#2.1, U1#2.24, U2#2.1, U2#2.24
/PULLUP_HIGH: R1.2, U1.2, U1.7, U1.9, U1.15, U2.2, U2.7, U2.9, U2.15, U3.2, U3.7, U3.9, U3.15, U4.2, U4.7, U4.9, U4.15, U5.2, U5.7, U5.9, U5.15, U6.2, U6.7, U6.9, U6.15, U7.2, U7.7, U7.9, U7.15, U8.2, U8.7, U8.9, U8.15
GND: C1.2, C1#2.2, C2.2, C3.31.2, C3.32.2, C4.2, C5V1.2, C5V2.2, CHIGH1.2, CHIGH2.2, CHIGH3.2, CHIGH4.2, CHIGH5.2, CHIGH6.2, CHIGH7.2, CHIGH8.2, CN7.8, CN7.19, CN7.20, CN7.22, CN10.9, CN10.20, J1.2, J1.4, J1.38, J1.40, J1#2.2, J1#2.4, J1#2.38, J1#2.40, J1#3.2, J1#3.4, J1#3.38, J1#3.40, J2#2.2, J2#2.4, J2#2.38, J2#2.40, J3#2.2, J6.1, J6.2, J6.3, J6.4, J6.5, J6.6, J6.7, J6.8, J7.1, J7.2, J7.3, J7.4, J7.5, J7.6, J7.7, J7.8, J8.1, J8.2, J8.3, J8.4, J8.5, J8.6, J8.7, J8.8, J9.1, J9.2, J9.3, J9.4, J9.5, J9.6, J9.7, J9.8, R2.2, U1.8, U1#2.4, U1#2.10, U1#2.15, U1#2.21, U1#2.28, U1#2.34, U1#2.39, U1#2.45, U2.8, U2#2.4, U2#2.10, U2#2.15, U2#2.21, U2#2.28, U2#2.34, U2#2.39, U2#2.45, U3.8, U4.8, U5.8, U6.8, U7.8, U8.8

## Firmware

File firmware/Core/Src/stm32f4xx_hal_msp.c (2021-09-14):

/* USER CODE BEGIN Header */
/**
  ******************************************************************************
  * @file         stm32f4xx_hal_msp.c
  * @brief        This file provides code for the MSP Initialization
  *               and de-Initialization codes.
  ******************************************************************************
  * @attention
  *
  * <h2><center>&copy; Copyright (c) 2021 STMicroelectronics.
  * All rights reserved.</center></h2>
  *
  * This software component is licensed by ST under BSD 3-Clause license,
  * the "License"; You may not use this file except in compliance with the
  * License. You may obtain a copy of the License at:
  *                        opensource.org/licenses/BSD-3-Clause
  *
  ******************************************************************************
  */
/* USER CODE END Header */

/* Includes ------------------------------------------------------------------*/
#include "main.h"
/* USER CODE BEGIN Includes */

/* USER CODE END Includes */

/* Private typedef -----------------------------------------------------------*/
/* USER CODE BEGIN TD */

/* USER CODE END TD */

/* Private define ------------------------------------------------------------*/
/* USER CODE BEGIN Define */

/* USER CODE END Define */

/* Private macro -------------------------------------------------------------*/
/* USER CODE BEGIN Macro */

/* USER CODE END Macro */

/* Private variables ---------------------------------------------------------*/
/* USER CODE BEGIN PV */

/* USER CODE END PV */

/* Private function prototypes -----------------------------------------------*/
/* USER CODE BEGIN PFP */

/* USER CODE END PFP */

/* External functions --------------------------------------------------------*/
/* USER CODE BEGIN ExternalFunctions */

/* USER CODE END ExternalFunctions */

/* USER CODE BEGIN 0 */

/* USER CODE END 0 */

void HAL_TIM_MspPostInit(TIM_HandleTypeDef *htim);
                                                                                                                                                                                                        /**
  * Initializes the Global MSP.
  */
void HAL_MspInit(void)
{
  /* USER CODE BEGIN MspInit 0 */

  /* USER CODE END MspInit 0 */

  __HAL_RCC_SYSCFG_CLK_ENABLE();
  __HAL_RCC_PWR_CLK_ENABLE();

  HAL_NVIC_SetPriorityGrouping(NVIC_PRIORITYGROUP_2);

  /* System interrupt init*/

  /* USER CODE BEGIN MspInit 1 */

  /* USER CODE END MspInit 1 */
}

/**
* @brief CRC MSP Initialization
* This function configures the hardware resources used in this example
* @param hcrc: CRC handle pointer
* @retval None
*/
void HAL_CRC_MspInit(CRC_HandleTypeDef* hcrc)
{
  if(hcrc->Instance==CRC)
  {
  /* USER CODE BEGIN CRC_MspInit 0 */

  /* USER CODE END CRC_MspInit 0 */
    /* Peripheral clock enable */
    __HAL_RCC_CRC_CLK_ENABLE();
  /* USER CODE BEGIN CRC_MspInit 1 */

  /* USER CODE END CRC_MspInit 1 */
  }

}

/**
* @brief CRC MSP De-Initialization
* This function freeze the hardware resources used in this example
* @param hcrc: CRC handle pointer
* @retval None
*/
void HAL_CRC_MspDeInit(CRC_HandleTypeDef* hcrc)
{
  if(hcrc->Instance==CRC)
  {
  /* USER CODE BEGIN CRC_MspDeInit 0 */

  /* USER CODE END CRC_MspDeInit 0 */
    /* Peripheral clock disable */
    __HAL_RCC_CRC_CLK_DISABLE();
  /* USER CODE BEGIN CRC_MspDeInit 1 */

  /* USER CODE END CRC_MspDeInit 1 */
  }

}

/**
* @brief TIM_Base MSP Initialization
* This function configures the hardware resources used in this example
* @param htim_base: TIM_Base handle pointer
* @retval None
*/
void HAL_TIM_Base_MspInit(TIM_HandleTypeDef* htim_base)
{
  if(htim_base->Instance==TIM1)
  {
  /* USER CODE BEGIN TIM1_MspInit 0 */

  /* USER CODE END TIM1_MspInit 0 */
    /* Peripheral clock enable */
    __HAL_RCC_TIM1_CLK_ENABLE();
  /* USER CODE BEGIN TIM1_MspInit 1 */

  /* USER CODE END TIM1_MspInit 1 */
  }
  else if(htim_base->Instance==TIM2)
  {
  /* USER CODE BEGIN TIM2_MspInit 0 */

  /* USER CODE END TIM2_MspInit 0 */
    /* Peripheral clock enable */
    __HAL_RCC_TIM2_CLK_ENABLE();
  /* USER CODE BEGIN TIM2_MspInit 1 */

  /* USER CODE END TIM2_MspInit 1 */
  }
  else if(htim_base->Instance==TIM3)
  {
  /* USER CODE BEGIN TIM3_MspInit 0 */

  /* USER CODE END TIM3_MspInit 0 */
    /* Peripheral clock enable */
    __HAL_RCC_TIM3_CLK_ENABLE();
  /* USER CODE BEGIN TIM3_MspInit 1 */

  /* USER CODE END TIM3_MspInit 1 */
  }
  else if(htim_base->Instance==TIM4)
  {
  /* USER CODE BEGIN TIM4_MspInit 0 */

  /* USER CODE END TIM4_MspInit 0 */
    /* Peripheral clock enable */
    __HAL_RCC_TIM4_CLK_ENABLE();
  /* USER CODE BEGIN TIM4_MspInit 1 */

  /* USER CODE END TIM4_MspInit 1 */
  }
  else if(htim_base->Instance==TIM5)
  {
  /* USER CODE BEGIN TIM5_MspInit 0 */

  /* USER CODE END TIM5_MspInit 0 */
    /* Peripheral clock enable */
    __HAL_RCC_TIM5_CLK_ENABLE();
  /* USER CODE BEGIN TIM5_MspInit 1 */

  /* USER CODE END TIM5_MspInit 1 */
  }
  else if(htim_base->Instance==TIM6)
  {
  /* USER CODE BEGIN TIM6_MspInit 0 */

  /* USER CODE END TIM6_MspInit 0 */
    /* Peripheral clock enable */
    __HAL_RCC_TIM6_CLK_ENABLE();
  /* USER CODE BEGIN TIM6_MspInit 1 */

  /* USER CODE END TIM6_MspInit 1 */
  }
  else if(htim_base->Instance==TIM8)
  {
  /* USER CODE BEGIN TIM8_MspInit 0 */

  /* USER CODE END TIM8_MspInit 0 */
    /* Peripheral clock enable */
    __HAL_RCC_TIM8_CLK_ENABLE();
  /* USER CODE BEGIN TIM8_MspInit 1 */

  /* USER CODE END TIM8_MspInit 1 */
  }
  else if(htim_base->Instance==TIM10)
  {
  /* USER CODE BEGIN TIM10_MspInit 0 */

  /* USER CODE END TIM10_MspInit 0 */
    /* Peripheral clock enable */
    __HAL_RCC_TIM10_CLK_ENABLE();
  /* USER CODE BEGIN TIM10_MspInit 1 */

  /* USER CODE END TIM10_MspInit 1 */
  }
  else if(htim_base->Instance==TIM11)
  {
  /* USER CODE BEGIN TIM11_MspInit 0 */

  /* USER CODE END TIM11_MspInit 0 */
    /* Peripheral clock enable */
    __HAL_RCC_TIM11_CLK_ENABLE();
  /* USER CODE BEGIN TIM11_MspInit 1 */

  /* USER CODE END TIM11_MspInit 1 */
  }
  else if(htim_base->Instance==TIM12)
  {
  /* USER CODE BEGIN TIM12_MspInit 0 */

  /* USER CODE END TIM12_MspInit 0 */
    /* Peripheral clock enable */
    __HAL_RCC_TIM12_CLK_ENABLE();
  /* USER CODE BEGIN TIM12_MspInit 1 */

  /* USER CODE END TIM12_MspInit 1 */
  }
  else if(htim_base->Instance==TIM13)
  {
  /* USER CODE BEGIN TIM13_MspInit 0 */

  /* USER CODE END TIM13_MspInit 0 */
    /* Peripheral clock enable */
    __HAL_RCC_TIM13_CLK_ENABLE();
  /* USER CODE BEGIN TIM13_MspInit 1 */

  /* USER CODE END TIM13_MspInit 1 */
  }
  else if(htim_base->Instance==TIM14)
  {
  /* USER CODE BEGIN TIM14_MspInit 0 */

  /* USER CODE END TIM14_MspInit 0 */
    /* Peripheral clock enable */
    __HAL_RCC_TIM14_CLK_ENABLE();
  /* USER CODE BEGIN TIM14_MspInit 1 */

  /* USER CODE END TIM14_MspInit 1 */
  }

}

void HAL_TIM_MspPostInit(TIM_HandleTypeDef* htim)
{
  GPIO_InitTypeDef GPIO_InitStruct = {0};
  if(htim->Instance==TIM1)
  {
  /* USER CODE BEGIN TIM1_MspPostInit 0 */

  /* USER CODE END TIM1_MspPostInit 0 */
    __HAL_RCC_GPIOA_CLK_ENABLE();
    /**TIM1 GPIO Configuration
    PA10     ------> TIM1_CH3
    */
    GPIO_InitStruct.Pin = GPIO_PIN_10;
    GPIO_InitStruct.Mode = GPIO_MODE_AF_PP;
    GPIO_InitStruct.Pull = GPIO_NOPULL;
    GPIO_InitStruct.Speed = GPIO_SPEED_FREQ_MEDIUM;
    GPIO_InitStruct.Alternate = GPIO_AF1_TIM1;
    HAL_GPIO_Init(GPIOA, &GPIO_InitStruct);

  /* USER CODE BEGIN TIM1_MspPostInit 1 */

  /* USER CODE END TIM1_MspPostInit 1 */
  }
  else if(htim->Instance==TIM2)
  {
  /* USER CODE BEGIN TIM2_MspPostInit 0 */

  /* USER CODE END TIM2_MspPostInit 0 */

    __HAL_RCC_GPIOB_CLK_ENABLE();
    /**TIM2 GPIO Configuration
    PB10     ------> TIM2_CH3
    */
    GPIO_InitStruct.Pin = GPIO_PIN_10;
    GPIO_InitStruct.Mode = GPIO_MODE_AF_PP;
    GPIO_InitStruct.Pull = GPIO_NOPULL;
    GPIO_InitStruct.Speed = GPIO_SPEED_FREQ_LOW;
    GPIO_InitStruct.Alternate = GPIO_AF1_TIM2;
    HAL_GPIO_Init(GPIOB, &GPIO_InitStruct);

  /* USER CODE BEGIN TIM2_MspPostInit 1 */

  /* USER CODE END TIM2_MspPostInit 1 */
  }
  else if(htim->Instance==TIM3)
  {
  /* USER CODE BEGIN TIM3_MspPostInit 0 */

  /* USER CODE END TIM3_MspPostInit 0 */

    __HAL_RCC_GPIOB_CLK_ENABLE();
    /**TIM3 GPIO Configuration
    PB5     ------> TIM3_CH2
    */
    GPIO_InitStruct.Pin = GPIO_PIN_5;
    GPIO_InitStruct.Mode = GPIO_MODE_AF_PP;
    GPIO_InitStruct.Pull = GPIO_NOPULL;
    GPIO_InitStruct.Speed = GPIO_SPEED_FREQ_LOW;
    GPIO_InitStruct.Alternate = GPIO_AF2_TIM3;
    HAL_GPIO_Init(GPIOB, &GPIO_InitStruct);

  /* USER CODE BEGIN TIM3_MspPostInit 1 */

  /* USER CODE END TIM3_MspPostInit 1 */
  }
  else if(htim->Instance==TIM4)
  {
  /* USER CODE BEGIN TIM4_MspPostInit 0 */

  /* USER CODE END TIM4_MspPostInit 0 */

    __HAL_RCC_GPIOB_CLK_ENABLE();
    /**TIM4 GPIO Configuration
    PB6     ------> TIM4_CH1
    */
    GPIO_InitStruct.Pin = GPIO_PIN_6;
    GPIO_InitStruct.Mode = GPIO_MODE_AF_PP;
    GPIO_InitStruct.Pull = GPIO_NOPULL;
    GPIO_InitStruct.Speed = GPIO_SPEED_FREQ_LOW;
    GPIO_InitStruct.Alternate = GPIO_AF2_TIM4;
    HAL_GPIO_Init(GPIOB, &GPIO_InitStruct);

  /* USER CODE BEGIN TIM4_MspPostInit 1 */

  /* USER CODE END TIM4_MspPostInit 1 */
  }
  else if(htim->Instance==TIM5)
  {
  /* USER CODE BEGIN TIM5_MspPostInit 0 */

  /* USER CODE END TIM5_MspPostInit 0 */

    __HAL_RCC_GPIOA_CLK_ENABLE();
    /**TIM5 GPIO Configuration
    PA0-WKUP     ------> TIM5_CH1
    */
    GPIO_InitStruct.Pin = GPIO_PIN_0;
    GPIO_InitStruct.Mode = GPIO_MODE_AF_PP;
    GPIO_InitStruct.Pull = GPIO_PULLDOWN;
    GPIO_InitStruct.Speed = GPIO_SPEED_FREQ_LOW;
    GPIO_InitStruct.Alternate = GPIO_AF2_TIM5;
    HAL_GPIO_Init(GPIOA, &GPIO_InitStruct);

  /* USER CODE BEGIN TIM5_MspPostInit 1 */

  /* USER CODE END TIM5_MspPostInit 1 */
  }
  else if(htim->Instance==TIM8)
  {
  /* USER CODE BEGIN TIM8_MspPostInit 0 */

  /* USER CODE END TIM8_MspPostInit 0 */

    __HAL_RCC_GPIOC_CLK_ENABLE();
    /**TIM8 GPIO Configuration
    PC7     ------> TIM8_CH2
    */
    GPIO_InitStruct.Pin = GPIO_PIN_7;
    GPIO_InitStruct.Mode = GPIO_MODE_AF_PP;
    GPIO_InitStruct.Pull = GPIO_NOPULL;
    GPIO_InitStruct.Speed = GPIO_SPEED_FREQ_LOW;
    GPIO_InitStruct.Alternate = GPIO_AF3_TIM8;
    HAL_GPIO_Init(GPIOC, &GPIO_InitStruct);

  /* USER CODE BEGIN TIM8_MspPostInit 1 */

  /* USER CODE END TIM8_MspPostInit 1 */
  }
  else if(htim->Instance==TIM10)
  {
  /* USER CODE BEGIN TIM10_MspPostInit 0 */

  /* USER CODE END TIM10_MspPostInit 0 */

    __HAL_RCC_GPIOB_CLK_ENABLE();
    /**TIM10 GPIO Configuration
    PB8     ------> TIM10_CH1
    */
    GPIO_InitStruct.Pin = GPIO_PIN_8;
    GPIO_InitStruct.Mode = GPIO_MODE_AF_PP;
    GPIO_InitStruct.Pull = GPIO_NOPULL;
    GPIO_InitStruct.Speed = GPIO_SPEED_FREQ_MEDIUM;
    GPIO_InitStruct.Alternate = GPIO_AF3_TIM10;
    HAL_GPIO_Init(GPIOB, &GPIO_InitStruct);

  /* USER CODE BEGIN TIM10_MspPostInit 1 */

  /* USER CODE END TIM10_MspPostInit 1 */
  }
  else if(htim->Instance==TIM11)
  {
  /* USER CODE BEGIN TIM11_MspPostInit 0 */

  /* USER CODE END TIM11_MspPostInit 0 */

    __HAL_RCC_GPIOB_CLK_ENABLE();
    /**TIM11 GPIO Configuration
    PB9     ------> TIM11_CH1
    */
    GPIO_InitStruct.Pin = GPIO_PIN_9;
    GPIO_InitStruct.Mode = GPIO_MODE_AF_PP;
    GPIO_InitStruct.Pull = GPIO_NOPULL;
    GPIO_InitStruct.Speed = GPIO_SPEED_FREQ_MEDIUM;
    GPIO_InitStruct.Alternate = GPIO_AF3_TIM11;
    HAL_GPIO_Init(GPIOB, &GPIO_InitStruct);

  /* USER CODE BEGIN TIM11_MspPostInit 1 */

  /* USER CODE END TIM11_MspPostInit 1 */
  }
  else if(htim->Instance==TIM13)
  {
  /* USER CODE BEGIN TIM13_MspPostInit 0 */

  /* USER CODE END TIM13_MspPostInit 0 */
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

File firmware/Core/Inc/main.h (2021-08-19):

/* USER CODE BEGIN Header */
/**
  ******************************************************************************
  * @file           : main.h
  * @brief          : Header for main.c file.
  *                   This file contains the common defines of the application.
  ******************************************************************************
  * @attention
  *
  * <h2><center>&copy; Copyright (c) 2021 STMicroelectronics.
  * All rights reserved.</center></h2>
  *
  * This software component is licensed by ST under BSD 3-Clause license,
  * the "License"; You may not use this file except in compliance with the
  * License. You may obtain a copy of the License at:
  *                        opensource.org/licenses/BSD-3-Clause
  *
  ******************************************************************************
  */
/* USER CODE END Header */

/* Define to prevent recursive inclusion -------------------------------------*/
#ifndef __MAIN_H
#define __MAIN_H

#ifdef __cplusplus
extern "C" {
#endif

/* Includes ------------------------------------------------------------------*/
#include "stm32f4xx_hal.h"

/* Private includes ----------------------------------------------------------*/
/* USER CODE BEGIN Includes */
#include "extramain.h"
/* USER CODE END Includes */

/* Exported types ------------------------------------------------------------*/
/* USER CODE BEGIN ET */

/* USER CODE END ET */

/* Exported constants --------------------------------------------------------*/
/* USER CODE BEGIN EC */

/* USER CODE END EC */

/* Exported macro ------------------------------------------------------------*/
/* USER CODE BEGIN EM */

/* USER CODE END EM */

void HAL_TIM_MspPostInit(TIM_HandleTypeDef *htim);

/* Exported functions prototypes ---------------------------------------------*/
void Error_Handler(void);

/* USER CODE BEGIN EFP */
void Error_Handler(void);
/* USER CODE END EFP */

/* Private defines -----------------------------------------------------------*/
#define TIM_TICK_FREQ 1000000
#define TIM_CLOCK_FREQ 80000000
#define SYS_CLOCK_FREQ 160000000
#define B1_Pin GPIO_PIN_13
#define B1_GPIO_Port GPIOC
#define USART_TX_Pin GPIO_PIN_2
#define USART_TX_GPIO_Port GPIOA
#define USART_RX_Pin GPIO_PIN_3
#define USART_RX_GPIO_Port GPIOA
#define TEST_GPIO_Pin GPIO_PIN_4
#define TEST_GPIO_GPIO_Port GPIOA
#define LD2_Pin GPIO_PIN_5
#define LD2_GPIO_Port GPIOA
#define TMS_Pin GPIO_PIN_13
#define TMS_GPIO_Port GPIOA
#define TCK_Pin GPIO_PIN_14
#define TCK_GPIO_Port GPIOA
#define SWO_Pin GPIO_PIN_3
#define SWO_GPIO_Port GPIOB
/* USER CODE BEGIN Private defines */

/* USER CODE END Private defines */

#ifdef __cplusplus
}
#endif

#endif /* __MAIN_H */

/************************ (C) COPYRIGHT STMicroelectronics *****END OF FILE****/

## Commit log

2021-08-24 Working on host-side code
    [channel_mapping.csv]
2021-08-26 Project restructured, hardware folder added
    [channel_mapping.csv, clockgen.kicad_pcb, clockgen.sch]
2021-08-27 Working on PCB
    [clockgen.kicad_pcb, clockgen.sch]
2021-08-29 Two PCBs are routed
    [STM_Morpho.dsn, STM_Morpho.kicad_pcb, STM_Morpho.sch, STM_Morpho2.dsn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]
2021-08-30 Screw terminal adapter added
    [STM_Morpho.dsn, STM_Morpho.kicad_pcb, STM_Morpho.sch, screw_adapter.dsn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]
2021-08-30 Renamed folers
    [STM_Morpho (copy 1).sch, STM_Morpho (copy 2).sch, STM_Morpho.csv, STM_Morpho.dsn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]
2021-08-31 All PCBs concatenated to single panel
    [alltogether.kicad_pcb]
2021-09-01 Host-side software is restructured and commented
    [STM_Morpho.csv]
2021-09-26 Added methods to access frames

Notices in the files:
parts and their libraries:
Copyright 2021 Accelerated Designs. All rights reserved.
